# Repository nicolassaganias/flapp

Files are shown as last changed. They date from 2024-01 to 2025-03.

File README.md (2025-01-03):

# Flapp

Proof-of-concept studies and lab scale setups are required which is a crucial path towards the emergence of new ideas and their transferability towards implementation. Such studies within research (academia or enterprise) are often limited by the availability of flexible, low-cost and portable devices that allow small configurations to be mounted, monitored and controlled.
The emergence of 3D printing, Arduino based environment and alternative source of supply pushed towards the Do-your-own (DYO) approach which is supported by online communities allowing for the development of cheap and interactive alternatives.

This work received the support of a fellowship from the “la Caixa” Foundation (ID 100010434). The fellowship code is LCF/BQ/PR21/11840009.

This Bluetooth Low Energy (BLE) App is responsible of gathering data values from different esp32-based sensor devices.
At the moment the app is designed for it to communicate with 6 types of water-sensing electronic sensors:
```
pH 
EC 
ORP 
Pressure 
Weight  (digital scales with RS232 or analog output)
Temperature
```
All this sensors can be connected at the same time and after finishing the experiment, be sent in .csv format to any e-mail address or saved in the internal mobile phone/tablet memory.

# App Usage Instructions
When the app is opened you see an empty screen where you can search new device by clicking in the magnifying glass icon.

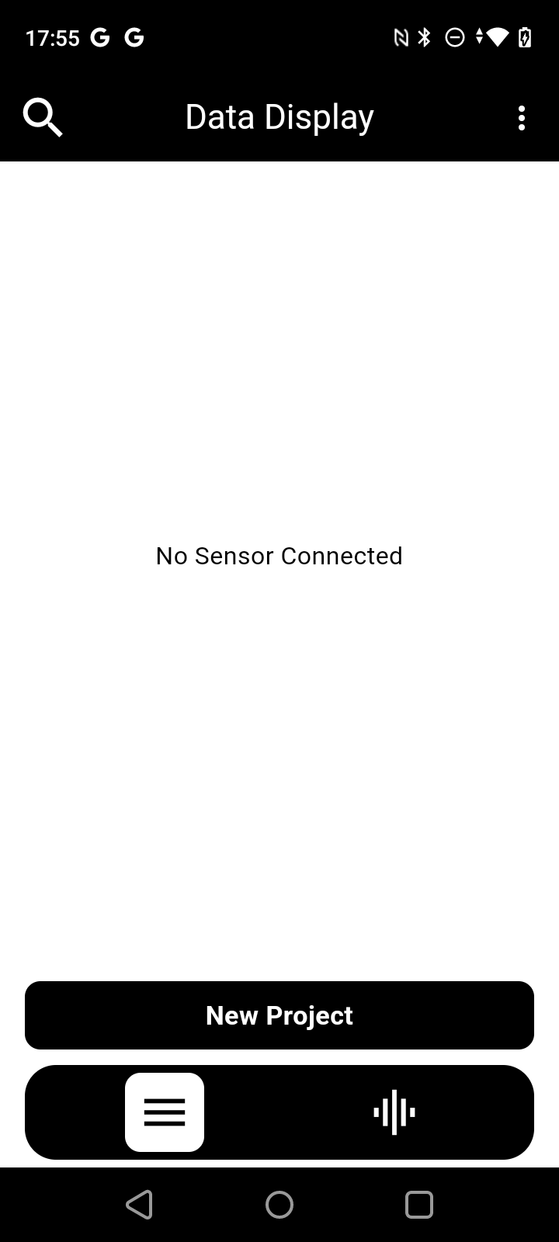
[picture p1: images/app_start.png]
Start Display


When you click the magnifying glass all the Bluetooth available devices are shown. 
Select the device/s to pair and start seeing data in real time.

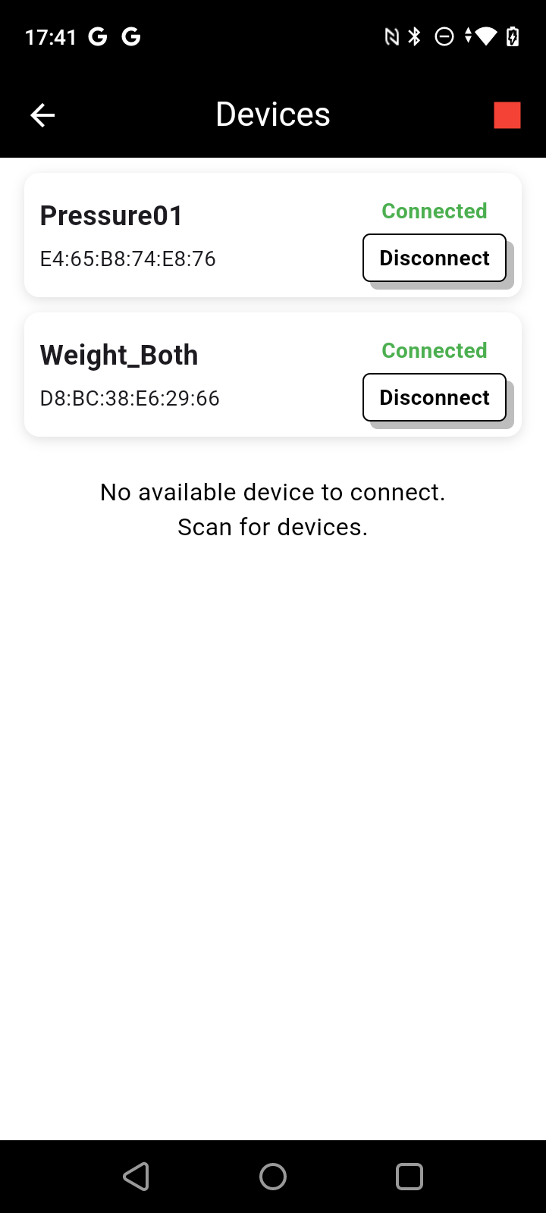
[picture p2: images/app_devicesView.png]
Devices Display


_maybe device will ask to pair with a new device. it is not necesary to pair with the device, the app will ask you to do it._

Once device is connected, see the data being received in Data Display:

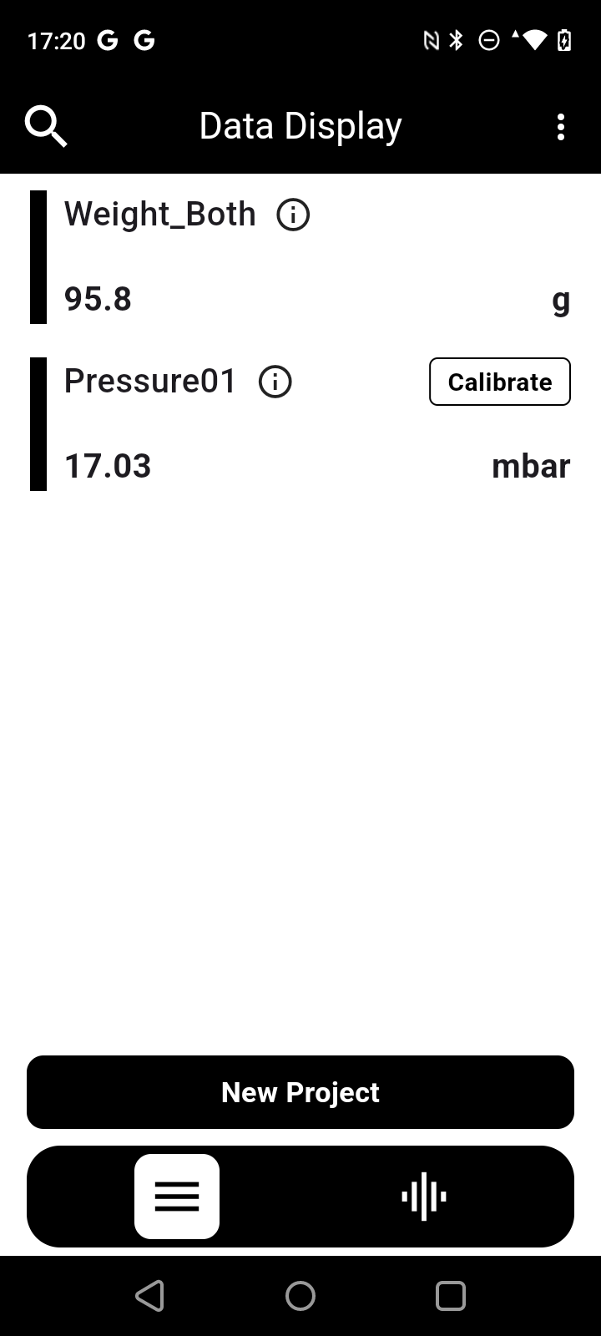
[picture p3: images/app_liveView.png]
Live View Display


User can Start a New Project to save the data for a period of time. Also user can adjust the interval in which the app will record the data values and also assign a project name:

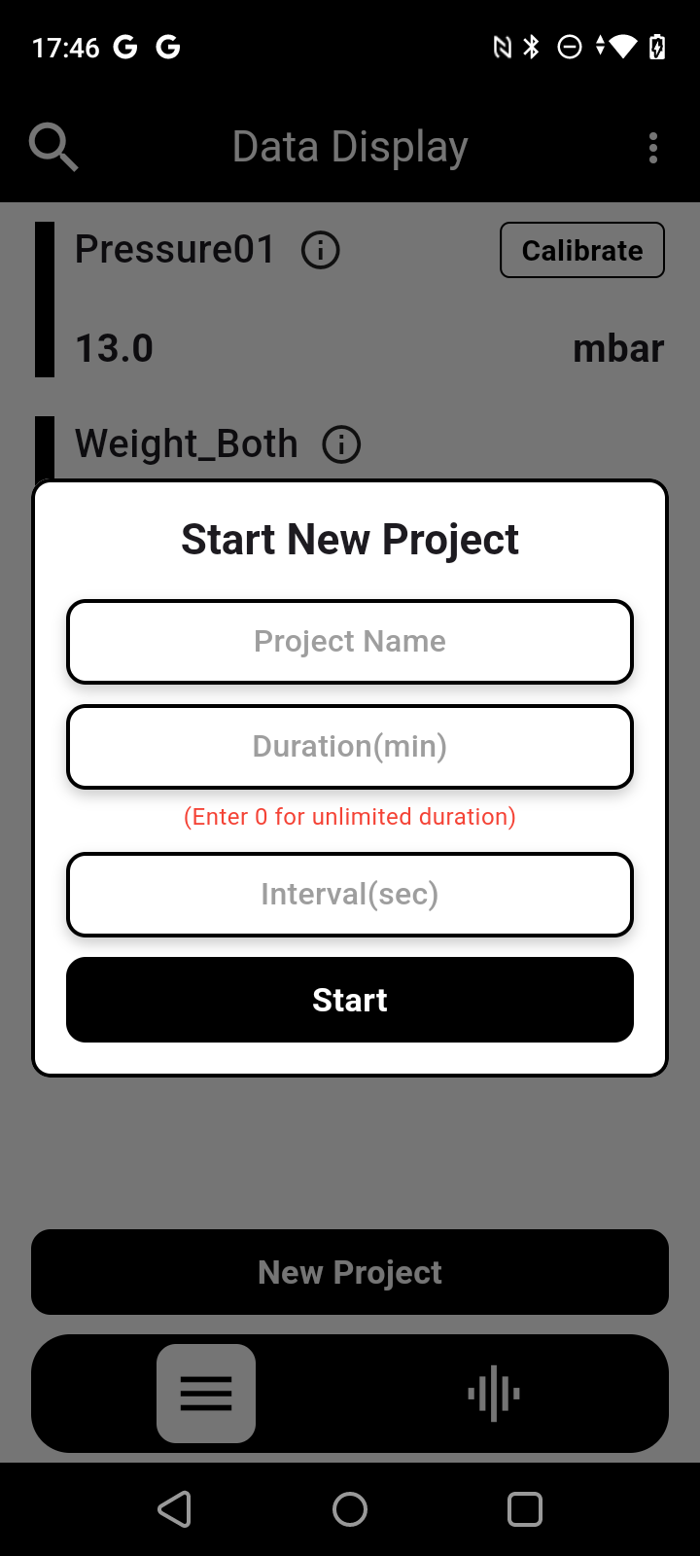
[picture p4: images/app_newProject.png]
New Project Display


When New Project's duration is over or button "Stop" is pressed, user will have the choice of sharing the data over e-mail or saving into the internal mobile memory

If Share is selected the app will bring up the default mail app and will compress the .csv file to be sent

Once data is shared user will be able to see a table-formated .csv file:

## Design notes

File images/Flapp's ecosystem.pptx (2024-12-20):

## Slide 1

FLAPP’S ECOSYSTEM

FLAPP (ANDROID APP)

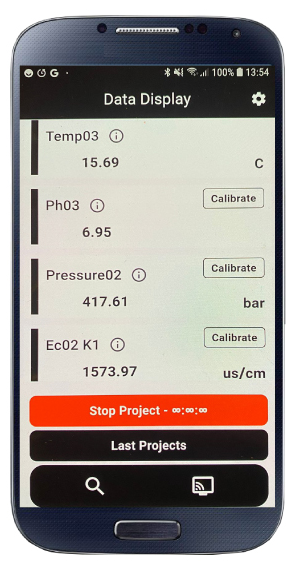
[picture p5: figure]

ARDUINO BASED SENSORS

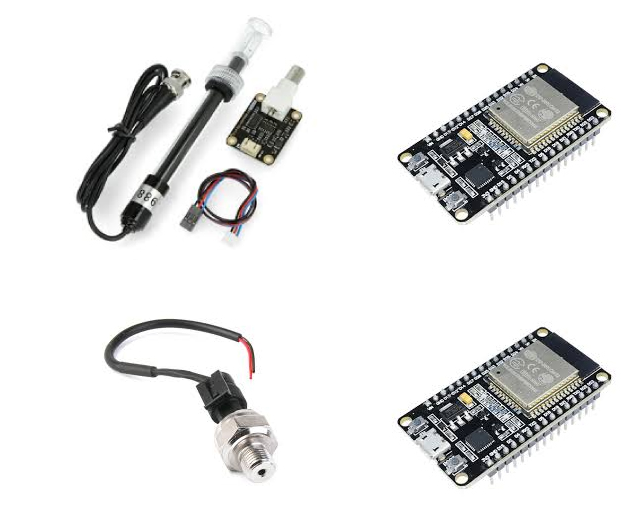
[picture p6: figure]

SAVING AND EXPORT DATA

pH
EC
ORP
Pressure
Weight
Temperature

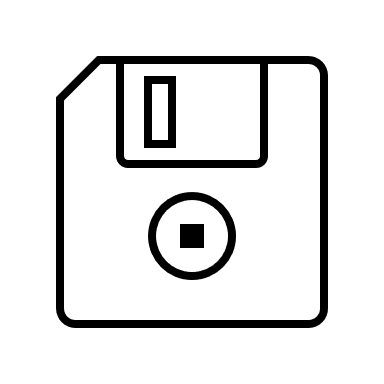
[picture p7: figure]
Disk outline

CSV file

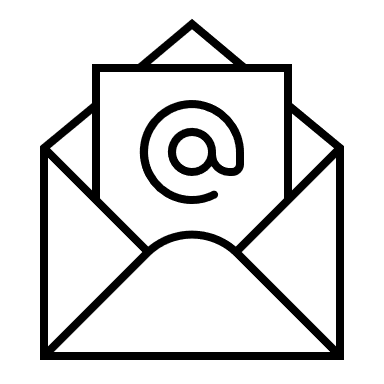
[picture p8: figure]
Email outline

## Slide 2

pH

EC

Pressure

Weight

Temperature

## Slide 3

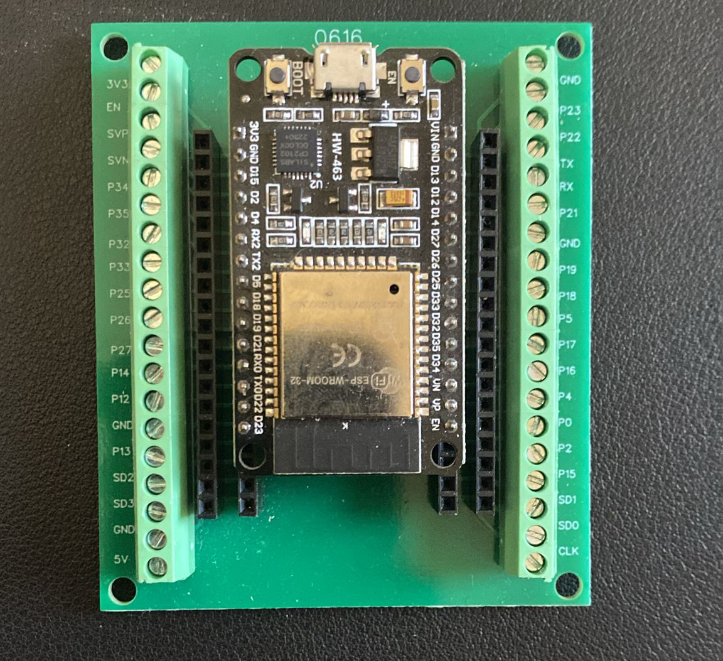
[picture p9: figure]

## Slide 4

FLAPP’S ECOSYSTEM

Pressure

Temperature

pH

EC

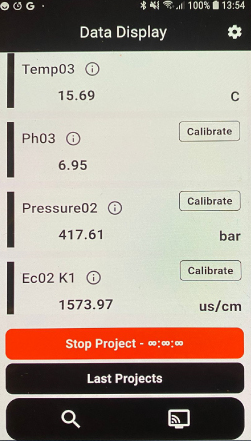
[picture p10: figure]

CSV file

10.2 g

Weight

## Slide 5

FLAPP’S ECOSYSTEM

Pressure detector

EC detector

Pressure

Temperature detector

pH

pH detector

CSV file

Weight detector

Temperature

EC

10.2 g

Weight

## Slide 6

FLAPP’S ECOSYSTEM

Electronic system

Temperature

Electronic system

Pressure

Electronic system

Electronic system

pH

EC

CSV file

10.2 g

Electronic system

Weight

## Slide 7

Pressure

Temperature

pH

EC

10.2 g

Weight

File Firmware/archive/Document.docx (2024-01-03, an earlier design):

pH Sensor

pH Sensor calibration command and status code for calibration feedback details:

Android App sends | ESP32 Response
pair | ph:pair
od | ph:<pH Value>
enterph | ph:<status code>
calph:<temperature> | ph: <status code>
exitph | ph: <status code>

When sends the calph:<temperature> from mobile app needs to send temperature which is previously recorded from the temperature sensor.

Status Code | Description
0 | Error Command
1 | Please put the probe into the 4.0 or 7.0 standard buffer solution
2 | Buffer Solution: 7.0 detected
3 | Buffer Solution: 4.0 detected
4 | Buffer Solution Error Try Again
5 | Calibration Successful
6 | Calibration Failed

ECSensor

EC Sensor calibration command and status code for calibration feedback details:

Android App sends | ESP32 Response
pair | ec:pair
od | ec:<EC Value>
enterec | ec:<status code>
calec:<temperature> | ec: <status code>
exitec | ec: <status code>

When sends the calec:<temperature> from mobile app needs to send temperature which is previously recorded from the temperature sensor.

Status Code | Description
0 | Error Command
1 | Please put the probe into the 1413us/cm or 2.76ms/cm or 12.88ms/cm buffer solution
2 | Buffer 1.413ms/cm
3 | Buffer 2.76ms/cm
4 | Buffer 12.88ms/cm
5 | Buffer Solution Error Try Again
6 | Calibration Successful
7 | Calibration Failed
8 | Successful, Send EXITEC to Save and Exit
9 | The computed value of K is out of range 0.5-2.0. Failed, Try Again

Pressure Sensor

Android App sends | ESP32 Response
pair | p:pair
od | p:<pressure Value>
enterp | p:<status code>
calp | p: <status code>
exitp | p: <status code>

Status Code | Description
1 | Enter calibration mode
2 | Successfully Calibrated
3 | Exit from calibration mode

Temperature Sensor

Android App sends | ESP32 Response
pair | t:pair
od | t:<temperature Value>

Weight Scale

Android App sends | ESP32 Response
pair | w:pair
od | w:<weight Value>

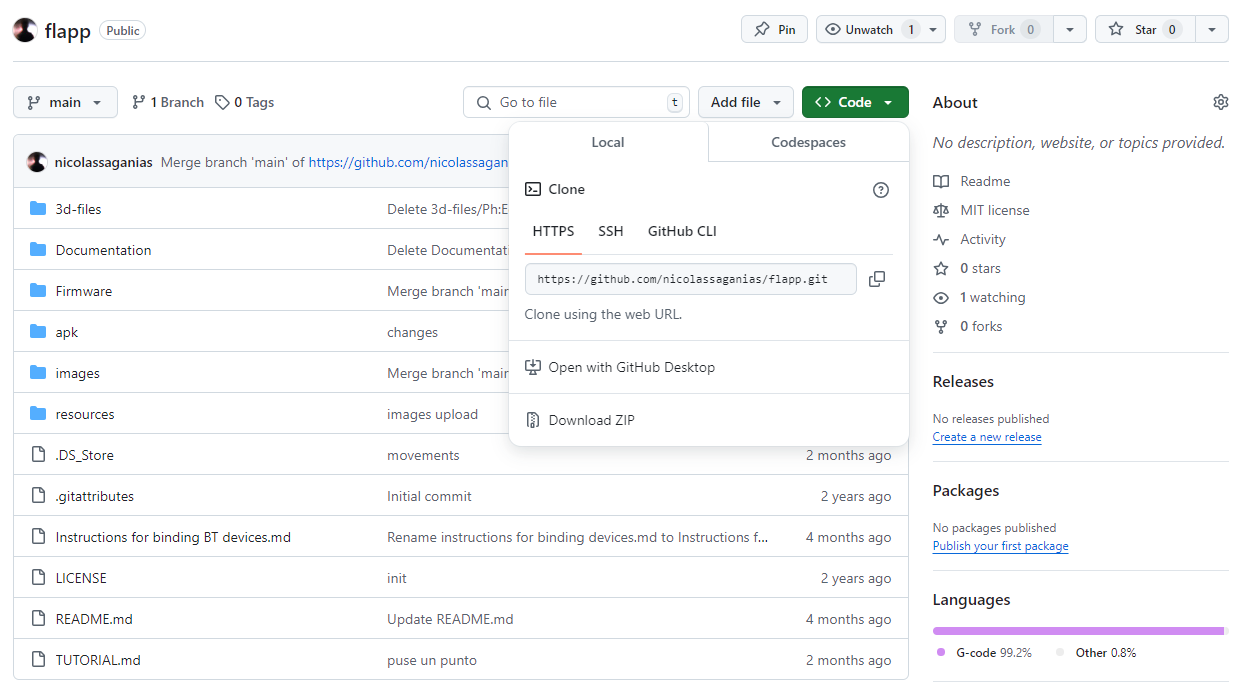
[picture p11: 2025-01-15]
images/help-githubZipDownload.png

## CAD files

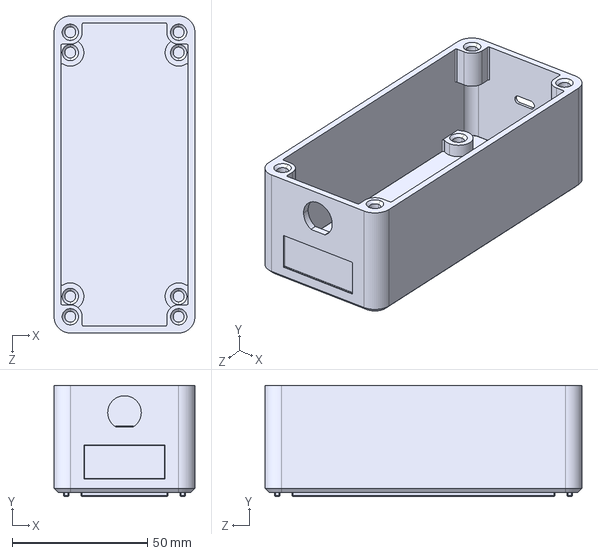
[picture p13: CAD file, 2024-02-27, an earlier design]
3d-files/old/BaseCaixaFDM_V4_model1.STEP
52.0 x 41.0 x 117.0 mm

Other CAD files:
3d-files/editables/Escotadura_tapa_metacrilato.DWG
3d-files/old/BaseCaixaFDM_V4_model3.STEP
3d-files/old/BaseCaixaFDM_V4_model2.STEP

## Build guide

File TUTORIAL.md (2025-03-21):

**FULL TUTORIAL UPDATED IN: https://docs.google.com/document/d/1VwzJdGcVvCzKNY8GULeiO_EsNGnJ2SCh/edit?usp=sharing&ouid=111671341203653565068&rtpof=true&sd=true**

**Flapp has different layer according to your knowlodge of Electronics and C++ Programming:**

**Layer 1: User.** Knows how to use the devices and the app.

**Layer 2: DIY/DIWO User.** Knows how to solder and upload code to ESP-32 board and can buy the Electronic components according to his/her needs

**Layer 3: Advanced User.** Knows how to modify systems and code and to make new devices. Makes contribution to Flapp community.

##Layer 1. User: Refer to "App Usage Instructions" in README.md file

##Layer 2: DIYO/DIWO User/s:

# Tutorial FLAPP

## Elements (Buylist)
- **ESP32/DFRobot pH Sensor Kit**
- **ESP32/DFRobot EC Sensor Kit**
- **ESP32/Pressure Sensor**
- **ESP32/RS232 Bluetooth Adapter + HC-05 Module**
- **ESP32/DFRobot Water Temperature Sensor**

---

## Connections

### pH Sensor
| ESP32 Pin | pH Sensor Pin |
|-----------|---------------|
| +3.3V     | Vcc (+)       |
| GND       | GND (-)       |
| 13        | Vout (A)      |

### EC Sensor
| ESP32 Pin | EC Sensor Pin |
|-----------|---------------|
| +3.3V     | Vcc (+)       |
| GND       | GND (-)       |
| 13        | Vout (A)      |

### Pressure Sensor
| ESP32 Pin | Pressure Sensor Pin |
|-----------|----------------------|
| +3.3V     | Vcc (+)              |
| GND       | GND (-)              |
| 13        | Vout (A)             |

### HC-05 Module
| ESP32 Pin | HC-05 Module Pin |
|-----------|-------------------|
| +3.3V     | Vcc (+)           |
| GND       | GND (-)           |
| 16        | TX                |
| 17        | RX                |

---

## Upload Sensor Codes

1. **Download and Install Arduino IDE**

2. **Download Codes from GitHub Repository**  
   - Navigate to the main GitHub repository.  
   - Click the green **Code** button and select **Download ZIP** to download all codes, or copy and paste the desired code into your Arduino IDE.  
   - After downloading, go to `/Firmware/ESP32_updated` and open the required code.

3. **Install Necessary Libraries**  
   - Ensure all required libraries are installed.

4. **Connect ESP32 to Computer**  
   - Use a micro USB cable to connect the ESP32 to your computer.

5. **Upload Desired Code**  
   - Upload the selected code to the ESP32.

6. **Install FLAPP App on Android Device**  
   - In the previously downloaded repository, navigate to `/apk` and download the latest `.apk` file.  
   - Transfer the `.apk` file to your Android device:  
     - One method is to upload the `.apk` to a cloud service (e.g., Google Drive) and download it on your Android device.  
   - Install the `.apk` by tapping on it.  
     - For more information, refer to [this guide](https://www.androidcentral.com/sideload-apps-how-guide).  
   - If prompted, click **Scan app** during installation.

7. **Open FLAPP App**  
   - Upon first launch, the app will request permissions:  
     - **Location Access:** You may decline this permission.  
     - **Device Discovery:** Accept this permission; otherwise, the app may not function correctly.

8. **Using the App**  
   - Refer to the `readme.md` file for detailed instructions.

---

## Troubleshooting

If you encounter issues such as:
- Unintended sensors connecting
- Incorrect sensor names
- `.csv` file not populating with values

You can resolve these by clearing the storage and cache data of the FLAPP app:

1. Press and hold the FLAPP app icon on your Android device.
2. Select **App Info** (or an **i** icon).
3. Clear the cache and storage data.

For more details, refer to [this guide on clearing cache in Android](https://www.androidcentral.com/how-and-when-clear-app-cache-or-data-android-device).

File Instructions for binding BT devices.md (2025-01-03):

# instructions for binding devices

For binding HC-05 module of weight sensor with bluetooth rs232 module.
AT commands for configurating ESP-32

** rs232 module needs the jumpers to be connected to "device" 
** to check the bluetooth address use "Bluetooth Scanner" app in android
** open file named "AT_COMANDS.ino"
++ use 9600 as Baud Rate and Both Ln and C 
** put hc-05 module into AT MODE: 
				1. unplug the module
				2. hold push button
				3. while holding plug the module
```
AT
AT+ROLE=1
AT+CMODE=0
AT+BIND=98D3,51,FEE015 // code for rs232 bluetooth module BC53 (new models) code for SH-B30 (old modules) is 0014,03,05071E or 6D
```
ESP32 sketch for communicating with HC-05 module through rx2 and tx2 (Serial2) like in our conection.
```
void setup()
{

  Serial.begin(9600);
  Serial.println("Enter AT commands:");
  Serial2.begin(38400);  // HC-05 default speed in AT command more
}

void loop()
{
  // Keep reading from HC-05 and send to Arduino Serial Monitor
  if (Serial2.available())
    Serial.write(Serial2.read());

  // Keep reading from Arduino Serial Monitor and send to HC-05
  if (Serial.available())
    Serial2.write(Serial.read());
}
```

# PIN FOR "B35" RS232_MODULE: 1234

# instructions for updating Flapp:
for devices connected to lequiamembranes google account:
1. long hold Flapp's icon
2. select "i" or "information" according to the device
3. clear all data (storage and caché)
4. uninstall the app
5. go to google drive app
6. look for Flapp's desired version, download and install

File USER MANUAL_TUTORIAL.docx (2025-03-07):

USER MANUAL: FLAPP + ARDUINO SENSORS

1 INTRODUCTION TO FLAPP’S ECOSYSTEM 2

2 HOW TO SET UP YOUR OWN SENSORS 3

2.1 Electroconductivity (EC) / pH sensor 3

2.1.1 Material 3

2.1.2 Set up the sensor 3

2.2 Pressure sensor 4

2.2.1 Material 4

2.2.2 Set up the sensor 5

2.3 Temperature sensor 5

2.3.1 Material 5

2.3.2 Set up the sensor 6

2.4 Weight sensor 7

2.4.1 Material 7

2.4.2 Set up the sensor 7

3 HOW TO UPLOAD SENSOR CODES WITH ARDUINO IDE 9

4 HOW TO INSTALL FLAPP APP IN ANDROID 10

5 HOW TO USE THE APP 11

# 1 INTRODUCTION TO FLAPP’S ECOSYSTEM

Can you imagine having complete control over your experiments with a low-cost sensor system built by yourself?

With this manual, you can not only collect accurate and customized data but also save money and learn essential tech skills while building tools tailored to your needs. This manual will guide you step by step to create your own sensor system, from the basics to a functional design, enabling you to monitor, measure, and record all the information from your projects efficiently and professionally. Innovation is in your hands!

What is FLAPP project about?

This project brings technology to life by combining cutting-edge software and hardware to create a powerful system of sensors and actuators. Designed for real-time monitoring and control, it’s perfect for personalized projects. The goal? To deliver a dynamic, cost-effective, and user-friendly solution that empowers scientists and citizens alike with access to high-quality data. Whether you’re a researcher, hobbyist, or data enthusiast, this project puts innovation and precision at your fingertips.

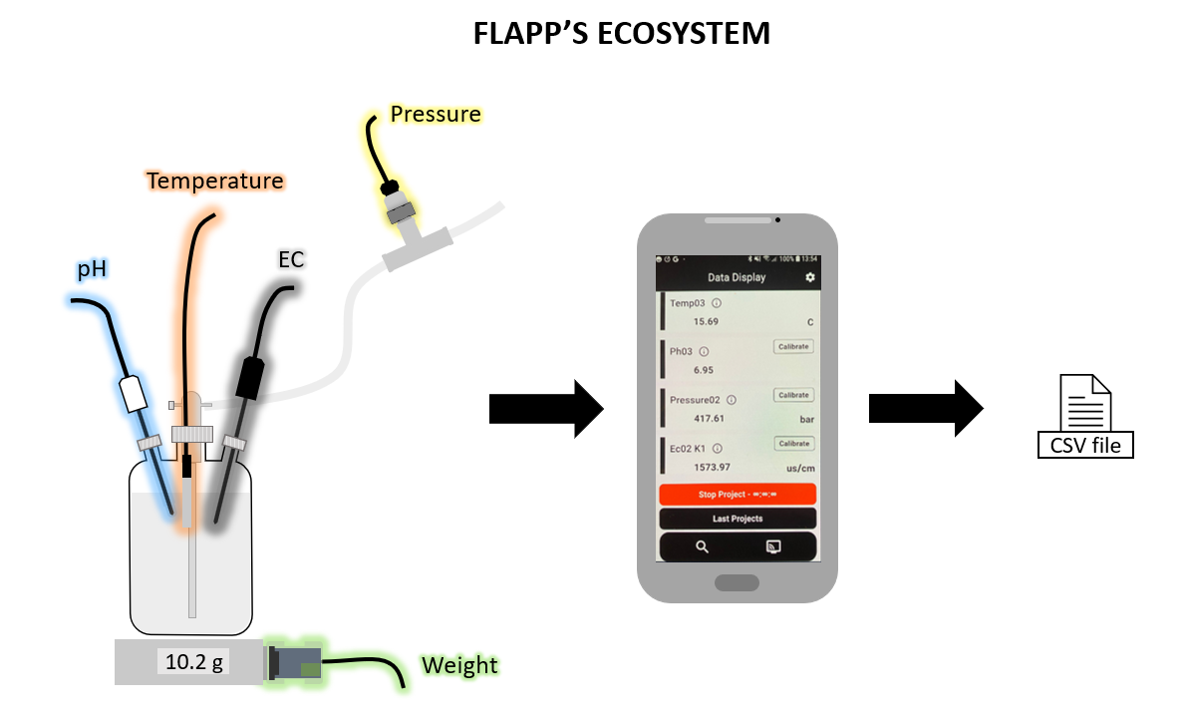
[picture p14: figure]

# 2 HOW TO SET UP YOUR OWN SENSORS

As tools, you will need at least one cutter, screwdriver and pliers.

First of all, we will recommend you remove all the packaging to dispose of all the material without having to make stops when you start to assemble the different sensors.

Click here to see all the videos of how to mount each sensor. (https://drive.google.com/drive/folders/1pJVmIqCvJQY8Tuv1QOb3zK2aEmzPpLRU?usp=sharing)

## 2.1 Electroconductivity (EC) / pH sensor

### 2.1.1 Material

Make sure you have all the material from the following table:

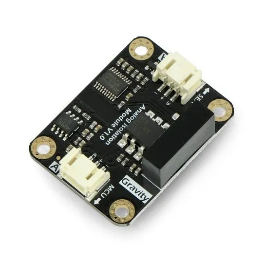
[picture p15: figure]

ESP32 | CONNECTION PLATE | ISOLATOR (optional)

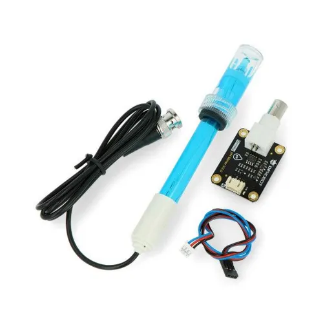
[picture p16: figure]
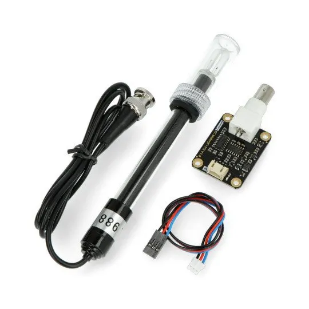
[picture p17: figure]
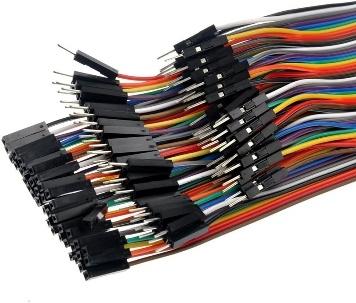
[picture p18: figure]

pH SENSOR | EC SENSOR | CABLES

### 2.1.2 Set up the sensor

1. Cut one side of the connection plate to fit the sensor into the box. Video link. (https://drive.google.com/file/d/1Bdlu-jHQMHMchdUJ4w0qhpB6GFINbjRV/view?usp=sharing)
2. Follow the schema below to set up the sensor:

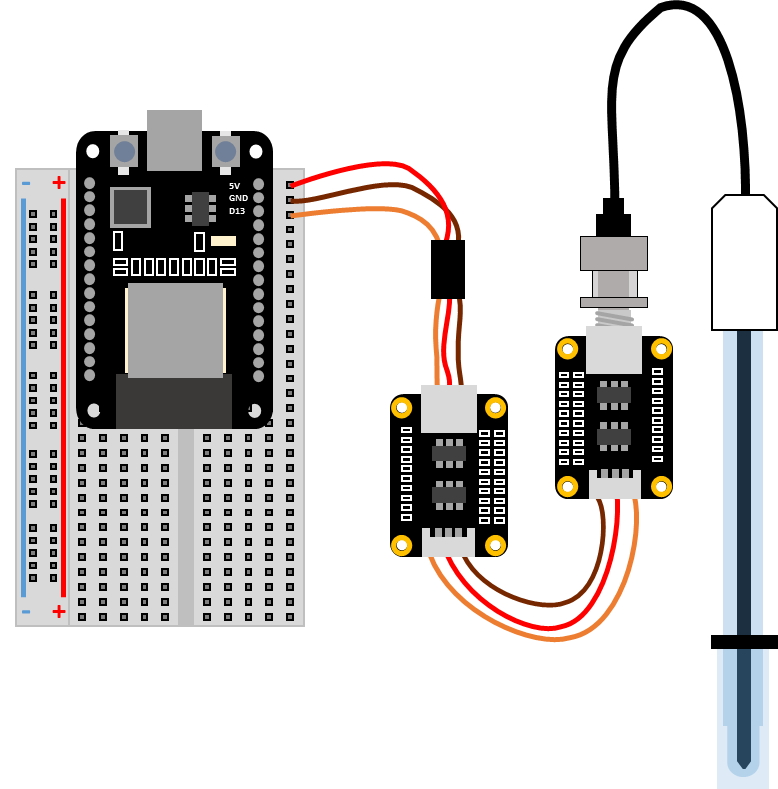
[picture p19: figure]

3. Connections needed are:

ESP32 pin | EC / pH Sensor Pin | Color in the scheme
+3.3v | Vcc (+) | Red
GND | GND (-) | Brown
13 | Vout (A) | Orange

## 2.2 Pressure sensor

### 2.2.1 Material

Make sure you have all the material from the following table:

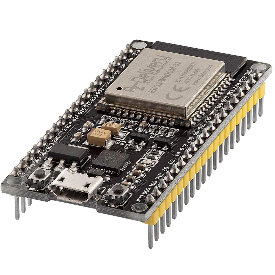
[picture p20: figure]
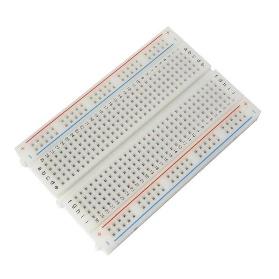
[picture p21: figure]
KIT MINI PARA ARDUINO CON UNO R3 (10 COMPONENTES)
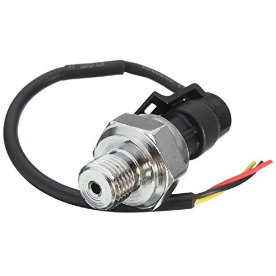
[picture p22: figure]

ESP32 | CONNECTION PLATE | PRESSURE SENSOR

### 2.2.2 Set up the sensor

1. Cut one side of the connection plate to fit the sensor into the box. Video link. (https://drive.google.com/file/d/1Bdlu-jHQMHMchdUJ4w0qhpB6GFINbjRV/view?usp=sharing)
2. Follow the schema below to set up the sensor:

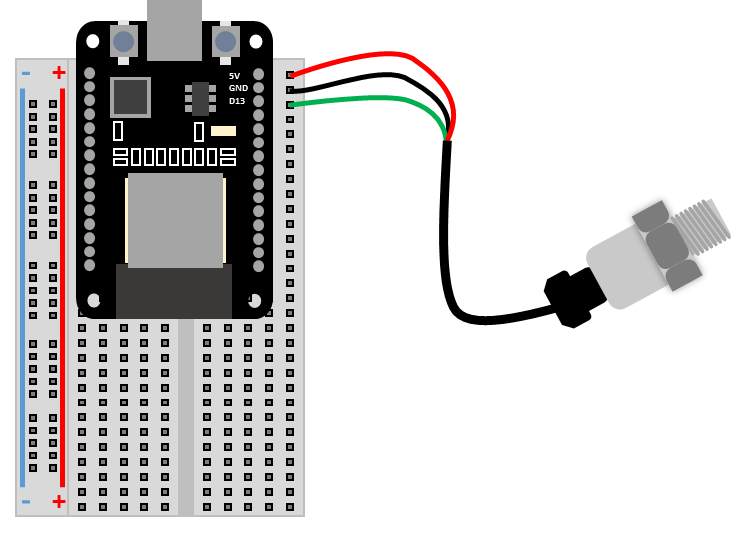
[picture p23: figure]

3. Connections needed are:

ESP32 pin | Pressure Sensor Pin | Color in the scheme
+3.3v | Vcc (+) | Red
GND | GND (-) | Black
13 | Vout (A) | Green

## 2.3 Temperature sensor

### 2.3.1 Material

Make sure you have all the material from the following table:

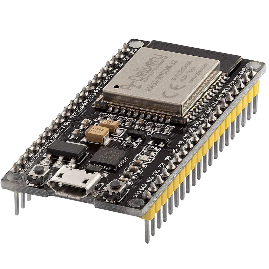
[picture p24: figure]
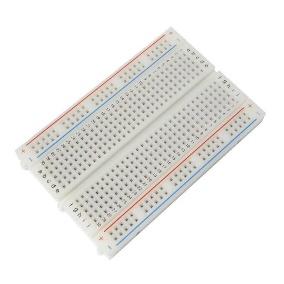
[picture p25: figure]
KIT MINI PARA ARDUINO CON UNO R3 (10 COMPONENTES)
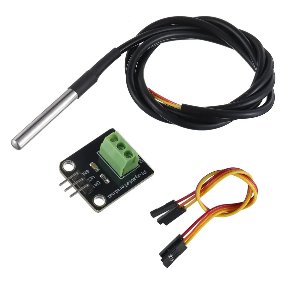
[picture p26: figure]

ESP32 | CONNECTION PLATE | TEMPERATURE SENSOR | CABLES

### 2.3.2 Set up the sensor

1. Cut one side of the connection plate to fit the sensor into the box. Video link. (https://drive.google.com/file/d/1Bdlu-jHQMHMchdUJ4w0qhpB6GFINbjRV/view?usp=sharing)
2. Follow the schema below to set up the sensor:

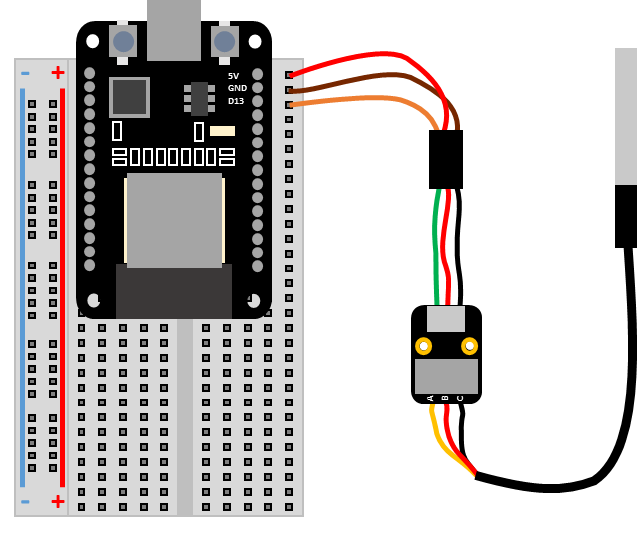
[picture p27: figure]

3. Connections needed are:

ESP32 pin | Pressure Sensor Pin | Color in the scheme
+3.3v | Vcc (+) | Red
GND | GND (-) | Brown
13 | Vout (A) | Orange

## 2.4 Weight sensor

### 2.4.1 Material

Make sure you have all the material from the following table:

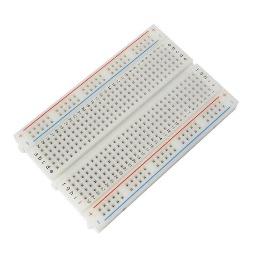
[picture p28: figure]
KIT MINI PARA ARDUINO CON UNO R3 (10 COMPONENTES)

ESP32 | CONNECTION PLATE | HC-05 MODULE

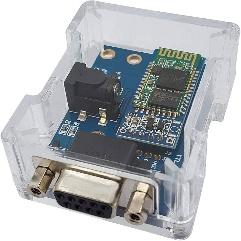
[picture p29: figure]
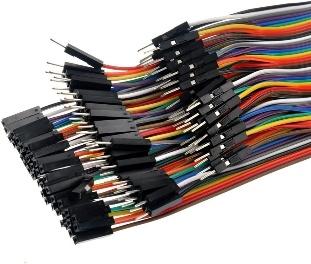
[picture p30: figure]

RS232 MODULE | CABLES

### 2.4.2 Set up the sensor

1. Cut one side of the connection plate to fit the sensor into the box. Video link. (https://drive.google.com/file/d/1Bdlu-jHQMHMchdUJ4w0qhpB6GFINbjRV/view?usp=sharing)
2. In this case, there are two possible options to set up the sensor: directly to the HC-05 module (a) or assembled on the connection plate (b):

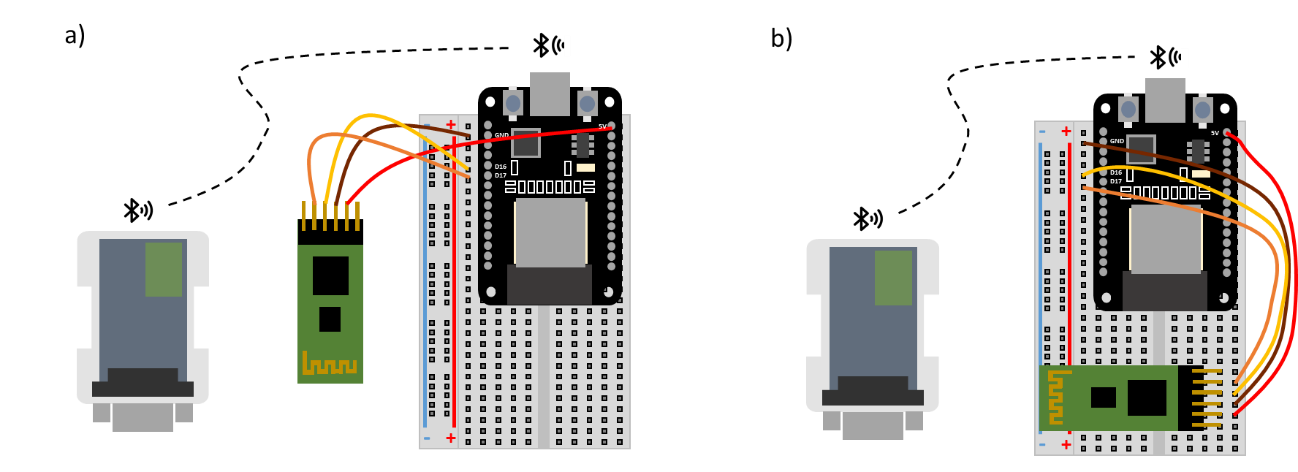
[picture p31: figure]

3. Connections needed are:

ESP32 pin | Pressure Sensor Pin | Color in the scheme
+5v | Vcc (+) | Red* (welded cable)
GND | GND (-) | Brown
16 | TX | Yellow
17 | RX | Orange

# 3 HOW TO UPLOAD SENSOR CODES WITH ARDUINO IDE

The following step is uploading the codes into each sensor. In this step you will need a computer.

1. Download and install Arduino IDE (https://support.arduino.cc/hc/en-us/articles/360019833020-Download-and-install-Arduino-IDE)
2. Install CH340 driver (https://sparks.gogo.co.nz/ch340.html)
3. Install CP210x Universal Windows Driver (https://www.silabs.com/documents/public/software/CP210x_Universal_Windows_Driver.zip)
  a. Unzip the folder.
  b. Click on “silabser” with the right button.
  c. Install it.
4. Open Arduino IDE and accept all the drivers that appear.
5. Install ESP32 board (https://randomnerdtutorials.com/installing-esp32-arduino-ide-2-0/) in Arduino IDE:
  a. Go to Install ESP32 Add-on in Arduino IDE.
  b. Follow the instructions.
  c. Install esp32 version 2.0.17.
6. Refer to the main github repository (https://github.com/nicolassaganias/flapp/tree/main) to download the codes.

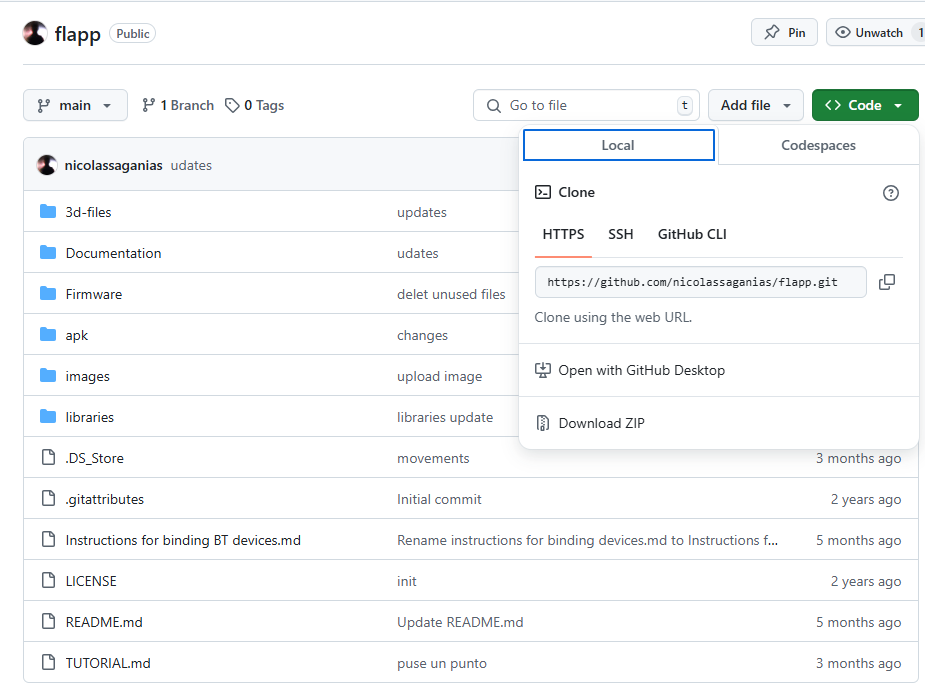
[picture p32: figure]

  a. To download from the github page go to the upper right green section “CODE” and click “download .zip file” to download all the codes or copy/paste to your arduino IDE.
  b. Once downloaded, unzip it and go to “/Firmware/ESP32_updated”.
  c. Open the code you need and look for the folder named after the sensor you are going to use.
  d. Open that folder and double click the .ino file to open it with Arduino IDE app.
7. In Arduino IDE program, go to “File/Preferences” and in “Sketchbook location” put the directory of the recently downloaded folder (“Flapp_main”). Be careful when you refer to the folder “Flapp_main” because when you unzip it, it generates a new folder. You should see the LIBRARIES folder and refer to the main FLAPP folder.
8. Connect ESP32 board to the computer with micro usb cable.
9. Upload desired Code. How to upload an arduino code? (https://support.arduino.cc/hc/en-us/articles/4733418441116-Upload-a-sketch-in-Arduino-IDE)
  a. Go to “Select board” and select the one related to your sensor (if you don’t know which one is, disconnect the sensor and you’ll see it).
  b. Search the “ESP32 Dev Module”:

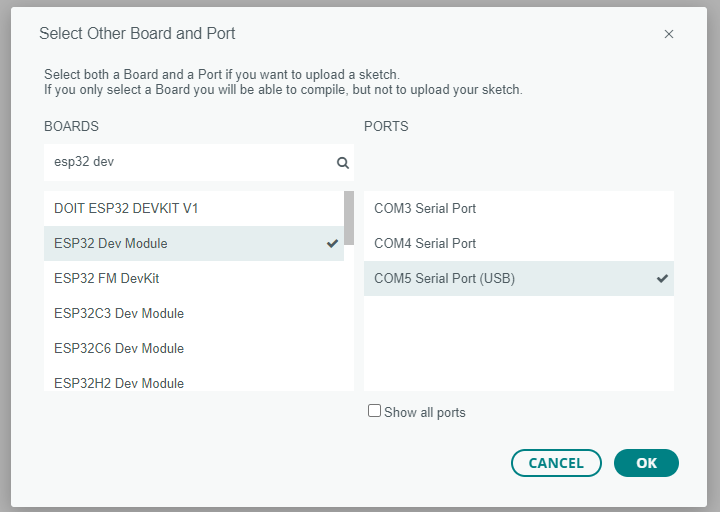
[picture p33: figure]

  c. Click “OK”
  d. Go to “Sketch” upper left corner and “Upload” (arrow button).

FAQs:

Is the weight sensor not displaying data in the app?

Probably the HC-05 module is not pairing to the RS232 module correctly. If the red light inside RS232 and also in HC-05 module is blinking continuously and fast it means that they are looking for devices to connect and so, they are not paired. To solve this issue refer to the github main repository in the file named "Instructions for binding BT devices.md". Link below:

https://github.com/nicolassaganias/flapp/blob/main/Instructions%20for%20binding%20%20BT%20devices.md

# 4 HOW TO INSTALL FLAPP APP IN ANDROID

Once you have your sensors assembled and with the code uploaded, the next step is installing the FLAPP app in your android device (apple is not yet available).

1. Install FLAPP app (.apk) to your android system (smartphone or tablet).
2. In the repository downloaded before, go to “/apk” and download the latest .apk file. This .apk file is the app that is going to be installed in your Android.
3. Now we have to transfer it to our Android. For that there are many ways, but we recommend putting the .apk into a cloud service (like Google Drive) and download it from the Android device. You can install .apk directly by clicking it. + info here (https://www.wikihow.com/Install-APK-Files-on-Android).
4. Install App and click “Scan app” if requested.
5. Open FLAPP app.
6. When opening the app for the first time you will be asked for some permissions:
  a. To enable location, you can say NO.
  b. To finding devices click YES (if not the system will not work).
7. Using the app: refer to “readme.md” file

# 5 HOW TO USE THE APP

The final step is learning how to use the app and save the data.

The app has 4 different screens:

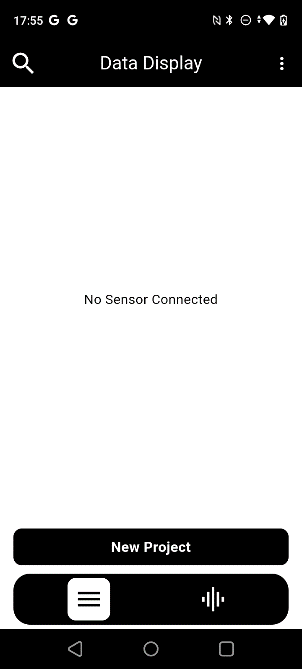
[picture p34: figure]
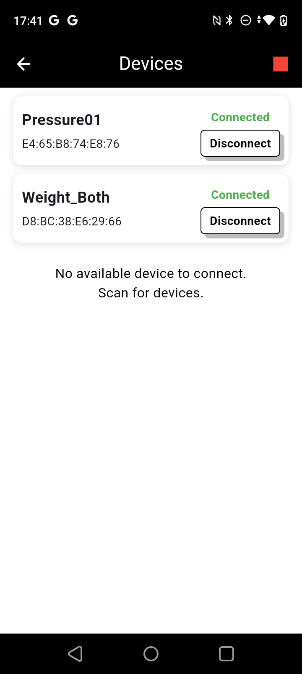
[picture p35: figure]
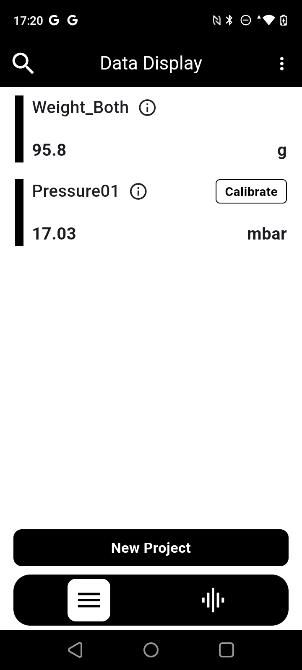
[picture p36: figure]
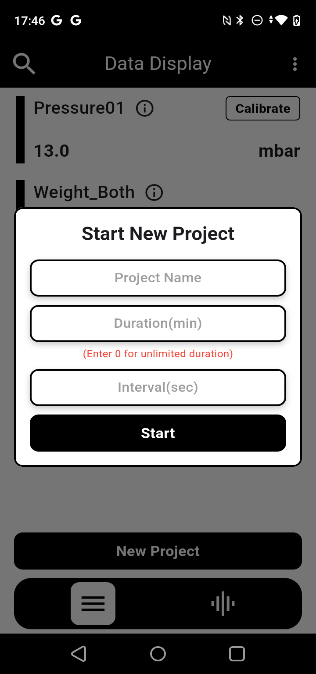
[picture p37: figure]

a) Search devices | b) Connect to it/them | c) Watch readings | d) Start a new project

1. When the app is opened you see an empty screen (a) where you can search new device by clicking in the magnifying glass icon.
2. When you click the magnifying glass all the Bluetooth available devices are shown (b). Select the device/s to pair and start seeing data in real time.
3. Once device is connected, see the data being received in Data Display (c).
4. To start a new project, click “New project” button.
5. Chose the name, the duration of the project and the interval between the data points.
6. Press “Start” to initiate the experiment. If you need to stop the experiment, just press “Stop” if not, it will stop once the duration is over.
7. When New Project's duration is over or button "Stop" is pressed, you will have to chose between sharing the data via e-mail or saving into the internal mobile memory.
8. Process your data using the .csv file.

Hints when using the app: If you encounter issues (p.e. non-desired sensors getting connected, wrong sensor names, .csv file not populating with values…) you can solve it by clearing storage and cache data of FLAPP app. To do this, you can hold FLAPP’s icon in the android device and press “app info” or “info” or just an “i” and clear caché and storage data or check how to clear cache in android (https://www.lifewire.com/clear-cache-android-4157780).

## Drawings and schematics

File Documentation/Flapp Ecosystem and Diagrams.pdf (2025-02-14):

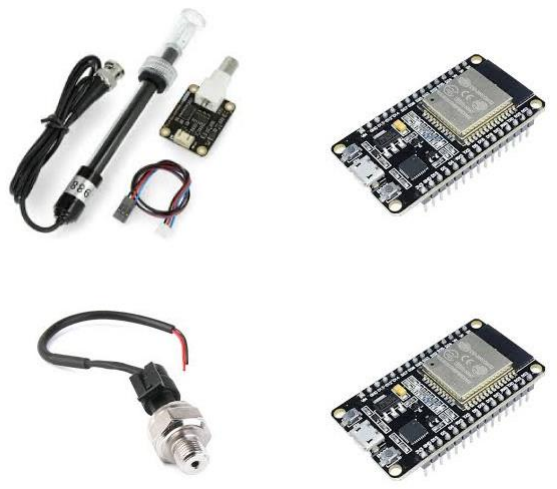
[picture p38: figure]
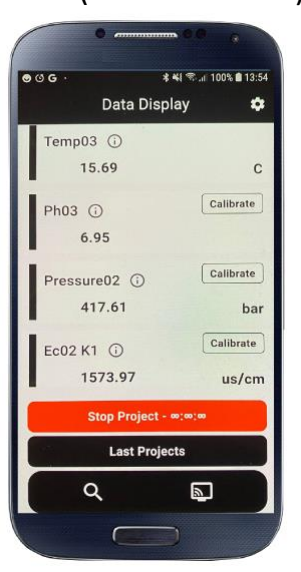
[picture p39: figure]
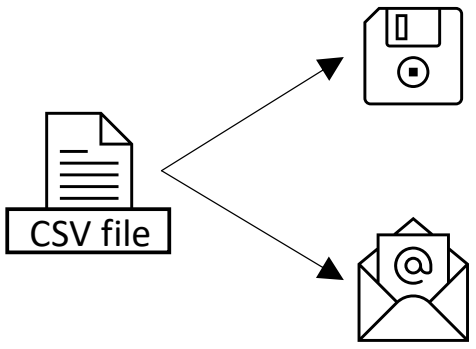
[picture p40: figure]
CSV file

ARDUINO BASED SENSORS | FLAPP (ANDROID APP) | SAVING AND EXPORT DATA

## FLAPP’S ECOSYSTEM

pH

EC

ORP

Pressure

Weight

Temperature

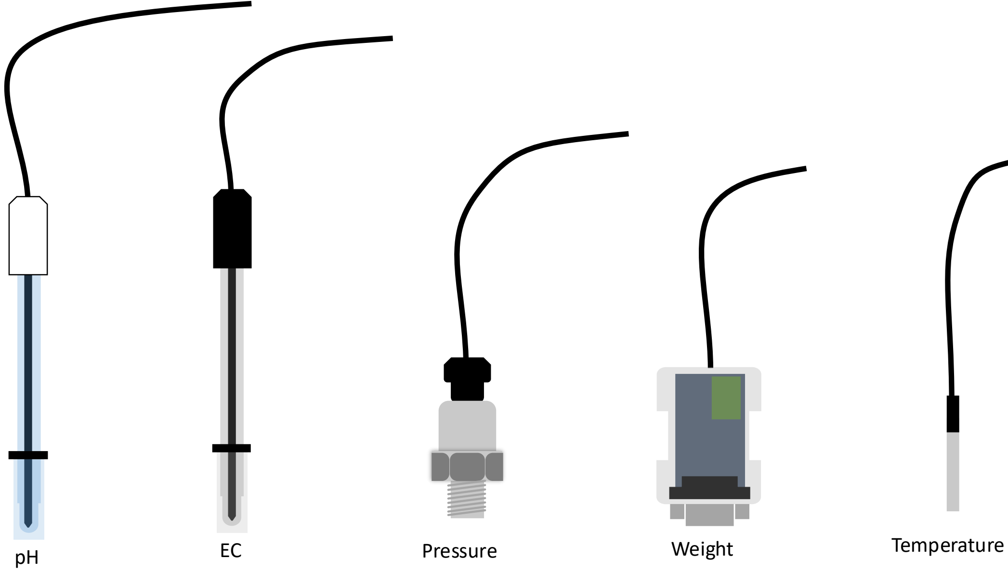
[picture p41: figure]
Pressure; Weight; Temperature
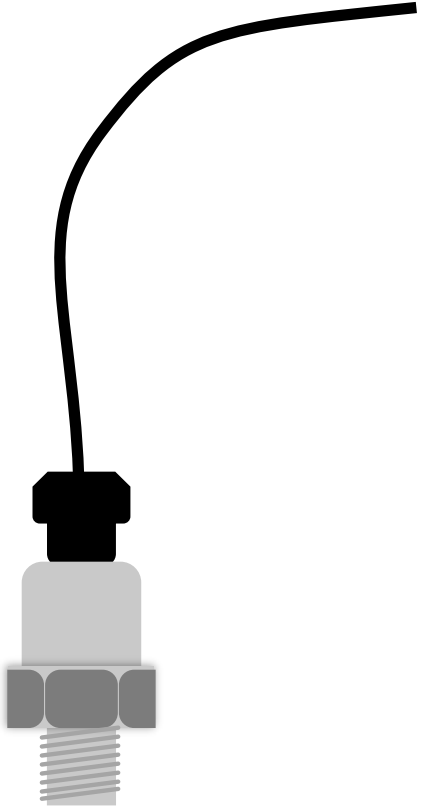
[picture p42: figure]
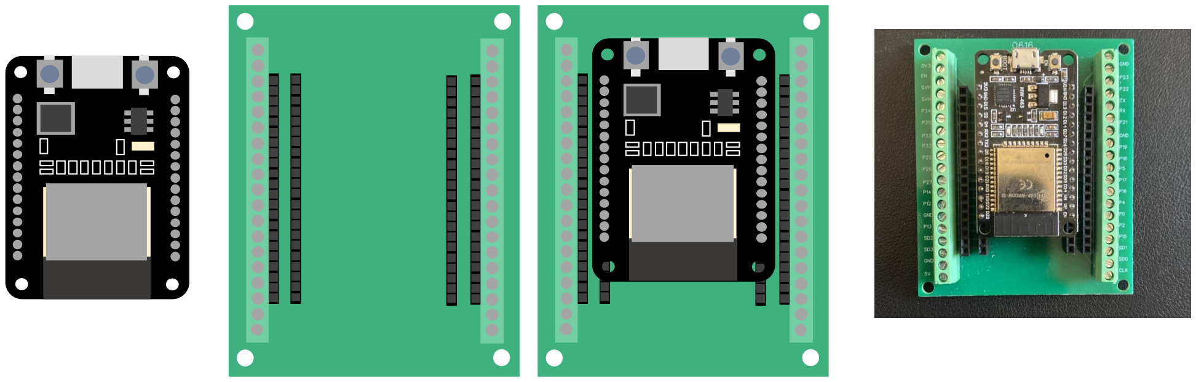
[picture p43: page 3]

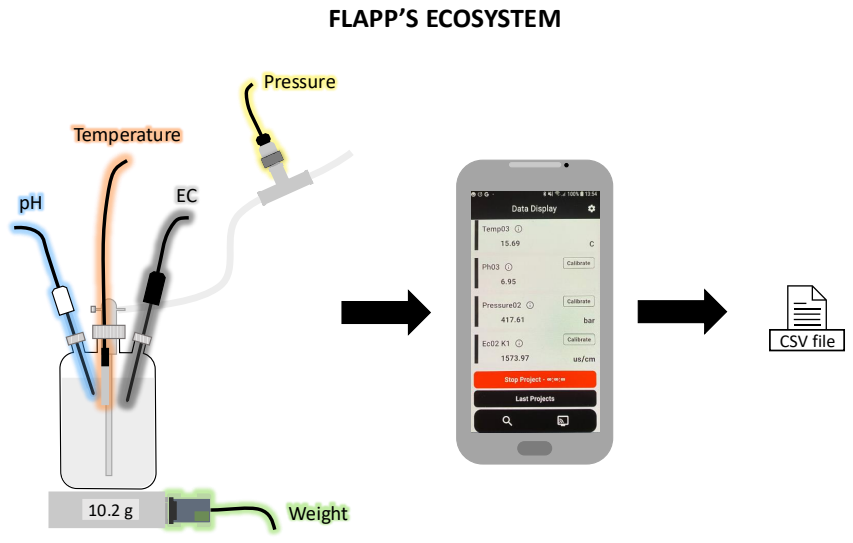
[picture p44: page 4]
Pressure; Weight; Temperature; CSV file

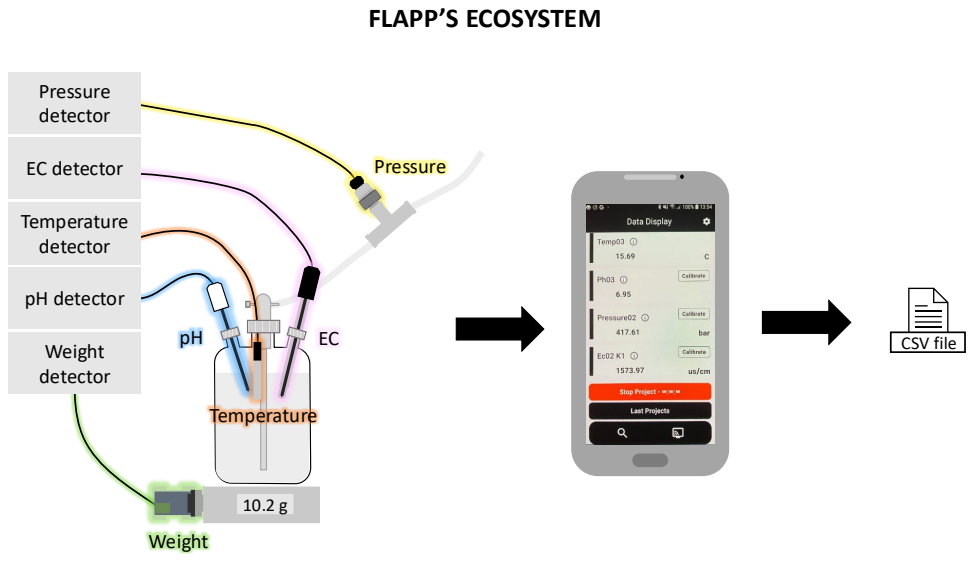
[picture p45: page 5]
Pressure; Weight; Temperature; CSV file; EC detector; Temperature detector; Pressure detector; pH detector; Weight detector

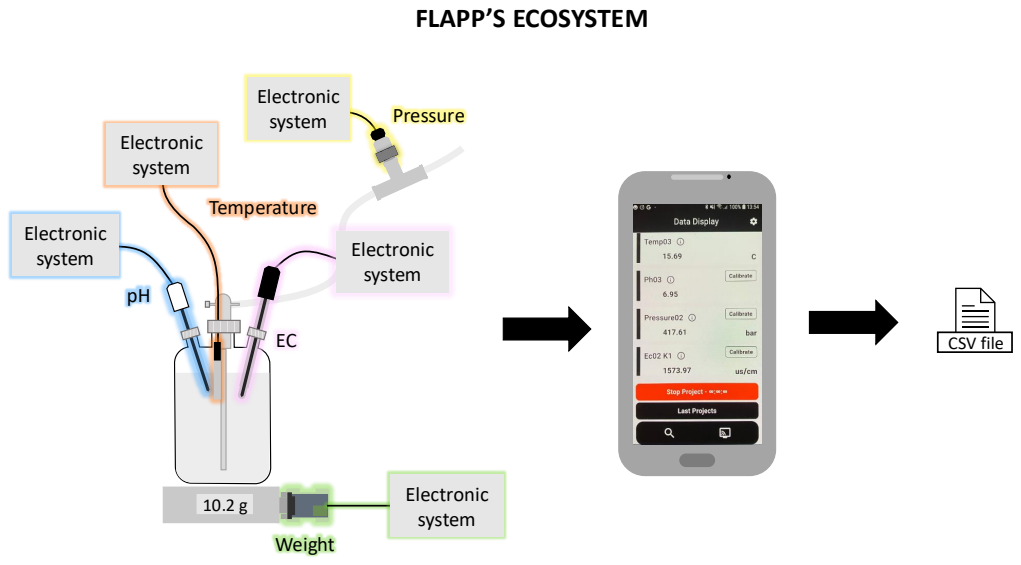
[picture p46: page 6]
Pressure; Weight; Temperature; CSV file; Electronic system

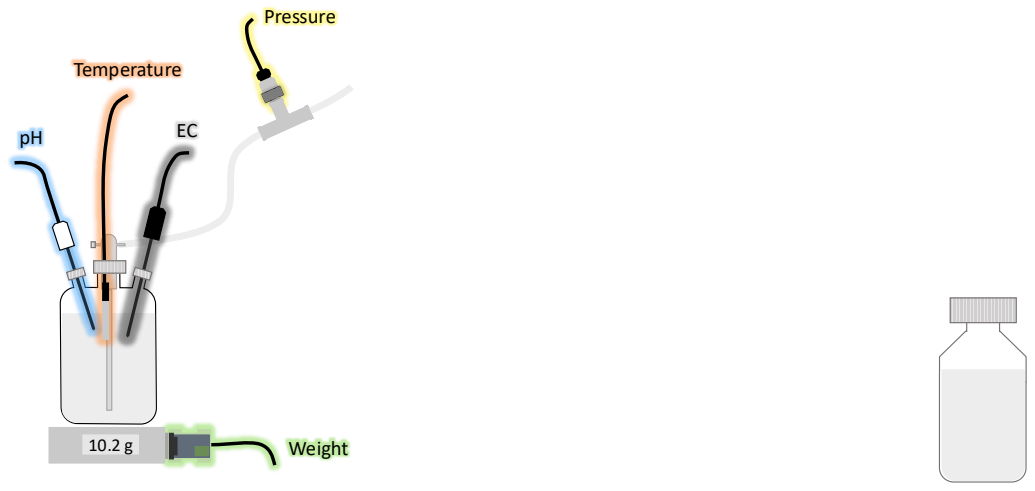
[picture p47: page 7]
Pressure; Weight; Temperature

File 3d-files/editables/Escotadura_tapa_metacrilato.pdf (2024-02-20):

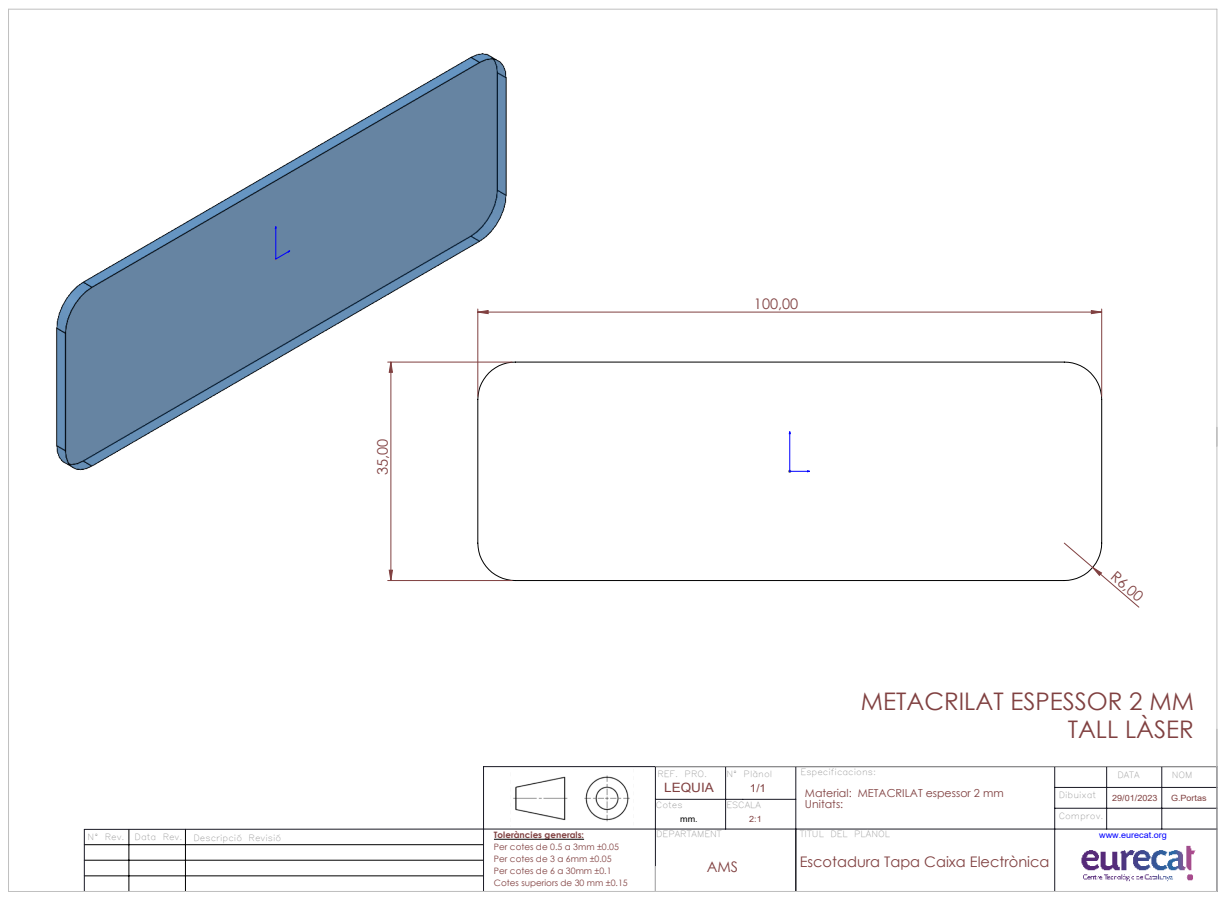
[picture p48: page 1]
TALL LÀSER

METACRILAT ESPESSOR 2 MM

REF. PRO. LEQUIA | Nº Plànol 1/1 | Especificacions: Material: METACRILAT espessor 2 mm Unitats: | | DATA | NOM

Dibuixat | 29/01/2023 | G.Portas
Comprov.

Cotes mm. | ESCALA 2:1

Nº Rev. | Data Rev. | Descripció Revisió | Toleràncies generals: Per cotes de 0.5 a 3mm ±0.05 Per cotes de 3 a 6mm ±0.05 Per cotes de 6 a 30mm ±0.1 Cotes superiors de 30 mm ±0.15 | DEPARTAMENT AMS | TÍTUL DEL PLÀNOL Escotadura Tapa Caixa Electrònica | www.eurecat.org

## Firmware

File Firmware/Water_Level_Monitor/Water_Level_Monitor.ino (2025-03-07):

#define WATER_LEVEL_SENSOR_PIN 32  // Pin connected to the water level sensor
#define RELAY_PIN 13               // Pin connected to the relay module
#define YELLOW_PIN 16
#define GREEN_PIN 17
#define BLUE_PIN 18
void setup() {
  pinMode(YELLOW_PIN, OUTPUT);
  digitalWrite(YELLOW_PIN, HIGH);
  delay(2000);
  pinMode(WATER_LEVEL_SENSOR_PIN, INPUT_PULLUP);  // The sensor normally stays HIGH
  pinMode(RELAY_PIN, OUTPUT);
  pinMode(BLUE_PIN, OUTPUT);
  pinMode(GREEN_PIN, OUTPUT);
  digitalWrite(RELAY_PIN, LOW);  // Ensure relay is off initially

  Serial.begin(115200);
  Serial.println("Water level monitoring started...");
  delay(1000);
}

void loop() {
  int waterLevel = digitalRead(WATER_LEVEL_SENSOR_PIN);

  Serial.print("Water Level Sensor: ");
  Serial.print(waterLevel);
  Serial.println(waterLevel == LOW ? " // Normal" : " // Overflow Detected");

  if (waterLevel == HIGH) {
    Serial.println("Water level exceeded! Turning on the pump...");
    digitalWrite(RELAY_PIN, LOW);  // Turn on relay (activating the pump)
    digitalWrite(GREEN_PIN, LOW);
    digitalWrite(BLUE_PIN, HIGH);
    delay(30000);  // Keep the pump running for 30 seconds

    Serial.println("Stopping the pump...");
    digitalWrite(RELAY_PIN, HIGH);  // Turn off relay
    digitalWrite(BLUE_PIN, LOW);
  } else {
    digitalWrite(GREEN_PIN, HIGH);
    digitalWrite(YELLOW_PIN, LOW);
    digitalWrite(BLUE_PIN, LOW);
  }
  delay(1000);  // Small delay before next reading
}

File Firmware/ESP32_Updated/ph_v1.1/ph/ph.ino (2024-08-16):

#define SensorPin 13            //pH meter Analog output to Arduino Analog Input 0
#define Offset 4.40            //deviation compensate
#define LED 13
#define samplingInterval 20
#define printInterval 800
#define ArrayLenth  40    //times of collection
int pHArray[ArrayLenth];   //Store the average value of the sensor feedback
int pHArrayIndex=0;
void setup(void)
{
  pinMode(LED,OUTPUT);
  Serial.begin(115200);
  Serial.println("pH meter experiment!");    //Test the serial monitor
}
void loop(void)
{
  static unsigned long samplingTime = millis();
  static unsigned long printTime = millis();
  static float pHValue,voltage;
  if(millis()-samplingTime > samplingInterval)
  {
      pHArray[pHArrayIndex++]=analogRead(SensorPin);
      if(pHArrayIndex==ArrayLenth)pHArrayIndex=0;
      voltage = avergearray(pHArray, ArrayLenth)*3.3/4095;
      pHValue = 3.5*voltage+Offset;
      samplingTime=millis();
  }
  if(millis() - printTime > printInterval)   //Every 800 milliseconds, print a numerical, convert the state of the LED indicator
  {
    Serial.print("Voltage:");
        Serial.print(voltage,2);
        Serial.print("    pH value: ");
    Serial.println(pHValue,2);
        digitalWrite(LED,digitalRead(LED)^1);
        printTime=millis();
  }
}
double avergearray(int* arr, int number){
  int i;
  int max,min;
  double avg;
  long amount=0;
  if(number<=0){
    Serial.println("Error number for the array to avraging!/n");
    return 0;
  }
  if(number<5){   //less than 5, calculated directly statistics
    for(i=0;i<number;i++){
      amount+=arr[i];
    }
    avg = amount/number;
    return avg;
  }else{
    if(arr[0]<arr[1]){
      min = arr[0];max=arr[1];
    }
    else{
      min=arr[1];max=arr[0];
    }
    for(i=2;i<number;i++){
      if(arr[i]<min){
        amount+=min;        //arr<min
        min=arr[i];
      }else {
        if(arr[i]>max){
          amount+=max;    //arr>max
          max=arr[i];
        }else{
          amount+=arr[i]; //min<=arr<=max
        }
      }//if
    }//for
    avg = (double)amount/(number-2);
  }//if
  return avg;
}

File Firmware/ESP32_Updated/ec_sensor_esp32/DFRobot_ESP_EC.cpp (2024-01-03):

/*
 * file DFRobot_ESP_EC.cpp * @ https://github.com/GreenPonik/DFRobot_ESP_EC_BY_GREENPONIK
 *
 * Arduino library for Gravity: Analog EC Sensor / Meter Kit V2, SKU: DFR0300
 * 
 * Based on the @ https://github.com/DFRobot/DFRobot_EC
 * Copyright   [DFRobot](http://www.dfrobot.com), 2018
 * Copyright   GNU Lesser General Public License
 *
 * ##################################################
 * ##################################################
 * ########## Fork on github by GreenPonik ##########
 * ############# ONLY ESP COMPATIBLE ################
 * ##################################################
 * ##################################################
 * 
 * version  V1.1.2
 * date  2019-06
 */

#include "Arduino.h"
#include "DFRobot_ESP_EC.h"
#include "EEPROM.h"

#define RES2 820.0
#define ECREF 200.0

DFRobot_ESP_EC::DFRobot_ESP_EC()
{
    this->_ecvalue = 0.0;
    this->_kvalue = 1.0;
    this->_kvalueLow = 1.0;
    this->_kvalueHigh = 1.0;
    this->_cmdReceivedBufferIndex = 0;
    this->_voltage = 0.0;
    this->_temperature = 25.0;
}

DFRobot_ESP_EC::~DFRobot_ESP_EC()
{
}

void DFRobot_ESP_EC::begin(int EepromStartAddress)
{
    this->_eepromStartAddress = EepromStartAddress;
    //check if calibration values (kvalueLow and kvalueHigh) are stored in eeprom
    this->_kvalueLow = EEPROM.readFloat(this->_eepromStartAddress); //read the calibrated K value from EEPROM
    if (this->_kvalueLow == float() || isnan(this->_kvalueLow) || isinf(this->_kvalueLow))
    {
        this->_kvalueLow = 1.0; // For new EEPROM, write default value( K = 1.0) to EEPROM
        EEPROM.writeFloat(this->_eepromStartAddress, this->_kvalueLow);
        EEPROM.commit();
    }

    this->_kvalueHigh = EEPROM.readFloat(this->_eepromStartAddress + (int)sizeof(float)); //read the calibrated K value from EEPROM
    if (this->_kvalueHigh == float() || isnan(this->_kvalueHigh) || isinf(this->_kvalueHigh))
    {
        this->_kvalueHigh = 1.0; // For new EEPROM, write default value( K = 1.0) to EEPROM
        EEPROM.writeFloat(this->_eepromStartAddress + (int)sizeof(float), this->_kvalueHigh);
        EEPROM.commit();
    }
    this->_kvalue = this->_kvalueLow; // set default K value: K = kvalueLow
}

float DFRobot_ESP_EC::readEC(float voltage, float temperature)
{
    float value = 0, valueTemp = 0;
    this->_rawEC = 1000 * voltage / RES2 / ECREF;
    Serial.print(F(">>>rawEC: "));
    Serial.print(this->_rawEC, 4);
    valueTemp = this->_rawEC * this->_kvalue;
    //automatic shift process
    //First Range:(0,2); Second Range:(2,20)
    if (valueTemp > 2.5)
    {
        this->_kvalue = this->_kvalueHigh;
    }
    else if (valueTemp < 2.0)
    {
        this->_kvalue = this->_kvalueLow;
    }

    value = this->_rawEC * this->_kvalue;                  //calculate the EC value after automatic shift
    value = value / (1.0 + 0.0185 * (temperature - 25.0)); //temperature compensation
    this->_ecvalue = value;                                //store the EC value for Serial CMD calibration
    Serial.print(F(", ecValue: "));
    Serial.print(this->_ecvalue, 4);
    Serial.println(F("<<<"));
    return this->_ecvalue;
}

int DFRobot_ESP_EC::calibration(float voltage, float temperature, char *cmd)
{
    this->_voltage = voltage;
    this->_temperature = temperature;
    //strupr(cmd);
    return ecCalibration(cmdParse(cmd)); // if received Serial CMD from the serial monitor, enter into the calibration mode
}

void DFRobot_ESP_EC::calibration(float voltage, float temperature)
{
    this->_voltage = voltage;
    this->_temperature = temperature;
    if (cmdSerialDataAvailable() > 0)
    {
        ecCalibration(cmdParse()); // if received Serial CMD from the serial monitor, enter into the calibration mode
    }
}

boolean DFRobot_ESP_EC::cmdSerialDataAvailable()
{
    char cmdReceivedChar;
    static unsigned long cmdReceivedTimeOut = millis();
    while (Serial.available() > 0)
    {
        if (millis() - cmdReceivedTimeOut > 500U)
        {
            this->_cmdReceivedBufferIndex = 0;
            memset(this->_cmdReceivedBuffer, 0, (ReceivedBufferLength));
        }
        cmdReceivedTimeOut = millis();
        cmdReceivedChar = Serial.read();
        if (cmdReceivedChar == '\n' || this->_cmdReceivedBufferIndex == ReceivedBufferLength - 1)
        {
            this->_cmdReceivedBufferIndex = 0;
            strupr(this->_cmdReceivedBuffer);
            return true;
        }
        else
        {
            this->_cmdReceivedBuffer[this->_cmdReceivedBufferIndex] = cmdReceivedChar;
            this->_cmdReceivedBufferIndex++;
        }
    }
    return false;
}

byte DFRobot_ESP_EC::cmdParse(const char *cmd)
{
    byte modeIndex = 0;
    if (strstr(cmd, "ENTEREC") != NULL)
        modeIndex = 1;
    else if (strstr(cmd, "EXITEC") != NULL)
        modeIndex = 3;
    else if (strstr(cmd, "CALEC") != NULL)
        modeIndex = 2;
    return modeIndex;
}

byte DFRobot_ESP_EC::cmdParse()
{
    byte modeIndex = 0;
    if (strstr(this->_cmdReceivedBuffer, "ENTEREC") != NULL)
        modeIndex = 1;
    else if (strstr(this->_cmdReceivedBuffer, "EXITEC") != NULL)
        modeIndex = 3;
    else if (strstr(this->_cmdReceivedBuffer, "CALEC") != NULL)
        modeIndex = 2;
    return modeIndex;
}

int DFRobot_ESP_EC::ecCalibration(byte mode)
{
    //char *receivedBufferPtr;
    static boolean ecCalibrationFinish = 0;
    static boolean enterCalibrationFlag = 0;
    static float compECsolution;
    float KValueTemp;
    switch (mode)
    {
    case 0:
        if (enterCalibrationFlag)
        {
            Serial.println(F(">>>Command Error<<<"));
            return 0;
        }
        break;

    case 1:
        enterCalibrationFlag = 1;
        ecCalibrationFinish = 0;
        Serial.println();
        Serial.println(F(">>>Enter EC Calibration Mode<<<"));
        Serial.println(F(">>>Please put the probe into the 1413us/cm or 2.76ms/cm or 12.88ms/cm buffer solution<<<"));
        Serial.println(F(">>>Only need two point for calibration one low (1413us/com) and one high(2.76ms/cm or 12.88ms/cm)<<<"));
        Serial.println();
        return 1;
        break;
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

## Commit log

2024-01-15 change ms/cm to us ec sensor
2024-02-19 Create instructions.md
    instructions for binding devices
2024-02-27 3d files
    [BaseCaixaFDM_V4_model1.STEP, BaseCaixaFDM_V4_model2.STEP, BaseCaixaFDM_V4_model3.STEP, Escotadura tapa.DWG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]
2024-09-19 Rename instructionsForBindingBtDevices.md to instructions for binding devices.md
2024-09-19 Rename instructions for binding devices.md to Instructions for binding BT devices.md
2025-03-07 user manual y 3ds
    [Escotadura tapa.DWG, Escotadura_tapa_metacrilato.DWG]
